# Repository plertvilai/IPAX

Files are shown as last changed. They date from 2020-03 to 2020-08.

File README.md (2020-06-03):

# In Situ Plankton Assemblage eXplorer
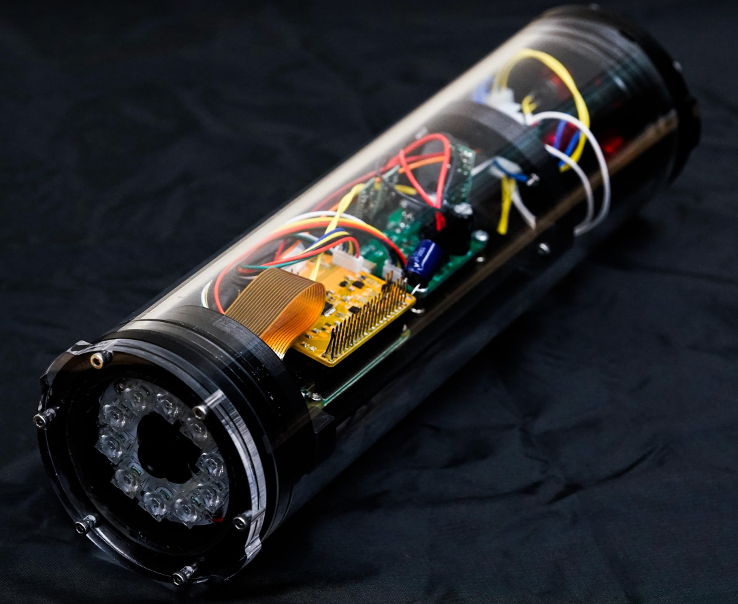
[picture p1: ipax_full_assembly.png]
Image of IPAX


This Github repository contains all information necessary to build the In Situ Plankton Assemblage eXplorer (IPAX). Here is a brief introduction to how to utilize the repository. 

# Detailed Guide

A detail building guide is given in the Building Guide subfolder. Note that this guide is written in HTML format. To read it, simply download the entire folder and use a browser to open the file [index.html](https://github.com/plertvilai/IPAX/blob/master/Building%20Guide/index.html "index.html"). 

# Fabrication Files

There are two folders containing files that are necessary for IPAX fabrication.
1. **Mechanicals** contains STL files that can be directly sent to a 3D printer to printout the mechanical parts. A STEP file is also included for users that are interested to develop the system further. The STEP file [Assembly Rev02 Revised for BES v3.step](https://github.com/plertvilai/IPAX/blob/master/Mechanicals/Assembly%20Rev02%20Revised%20for%20BES%20v3.step "Assembly Rev02 Revised for BES v3.step") contains CAD files of all the parts, including waterproof housing from Bluerobotics that can be opened with a CAD software for further development.
2. **PCBs** contains all files for the printed circuit boards in the IPAX. Each subfolder is for each PCB, and the folder fabrication contains Gerber files that can be sent directly to PCB manufacturers. Each subfolder also contains KiCAD files that users can use to develop the PCBs for fit their needs. 

# Firmware
The folder Firmware contains all software for the IPAX. 
### Control Board
This subfolder contains Arduino (.ino) files that can be uploaded to the control board of the IPAX. 
1. full_control_alwaysON is the main routine for the control board that set the Raspberry Pi to always ON.
2. full_control_interval is the main routine for the control board that turns the Raspberry Pi ON only at the specified time.
3. rtc_set is a temporary code that can be uploaded to the control board to set the real-time clock.

### Raspberry Pi
This subfolder contains Python files for the Raspberry Pi on the IPAX. 
1. connectArduino.py is a routine that allows the Raspberry Pi to communicate with the Arduino on the control board.
2. ipaxClass.py is the library for the IPAX.
3. ipaxDeploy.py is the main routine for deploying the IPAX.
4. shutdowncheck.py is the control script that allows the Raspberry Pi to be properly shutdown with an external switch on the housing and the control board.

The configuration subfolder contains all the configuration files needed to configure that Raspberry Pi.

# Bill of Materials
The folder BOM contains a single MS Excel file (.xlsx) that contains the detailed bill of materials of the IPAX.

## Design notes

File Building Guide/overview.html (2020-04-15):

# IPAX Documentation

1. Home
2. Overview

# Overview

Last updated: April, 2020

## Production Steps

This section outlines the production process of the IPAX. Though not necessarily needed to be done in this particular order, we recommend users to build an IPAX in the step as shown in the diagram below. This page provides steps for assembly process, but the detail of each step can be found in the respective page.

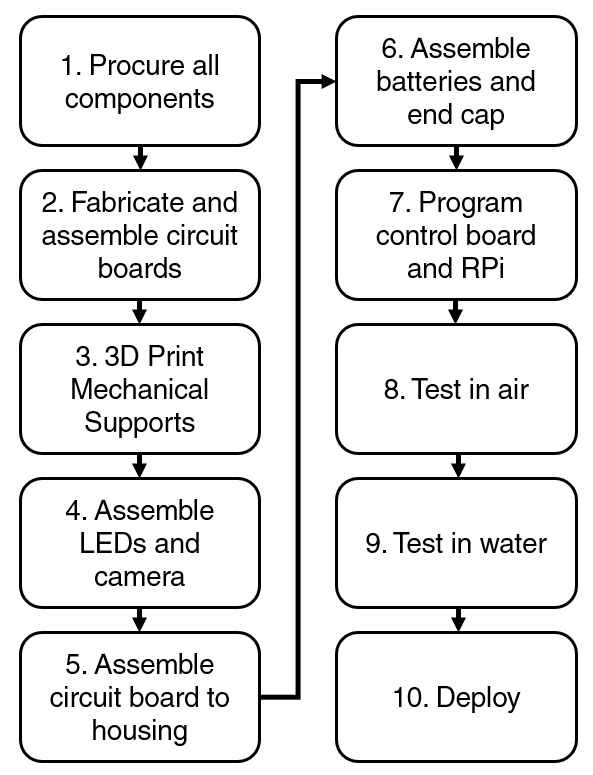
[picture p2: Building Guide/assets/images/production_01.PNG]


## 1. Procurement

The entire bill of materials for the IPAX is provided in the BOM folder. The BOM also indicates recommended vendors, though users can procure their components through any vendors.

## 2. Printed Circuit Boards

There are 3 printed circuit boards in the IPAX that need to be fabricated. The KiCAD files for all three boards are available in the PCBs folder. In each folder for each PCB, there is a folder called "Gerber" that contains gerber files that are ready to be sent to a PCB house for fabrication.

The control board and the power regulator boards can be fabricated with regular FR-4 substrate, but we strongly recommend that the LED array board should be fabricated with aluminum substrate to help with heat sink.

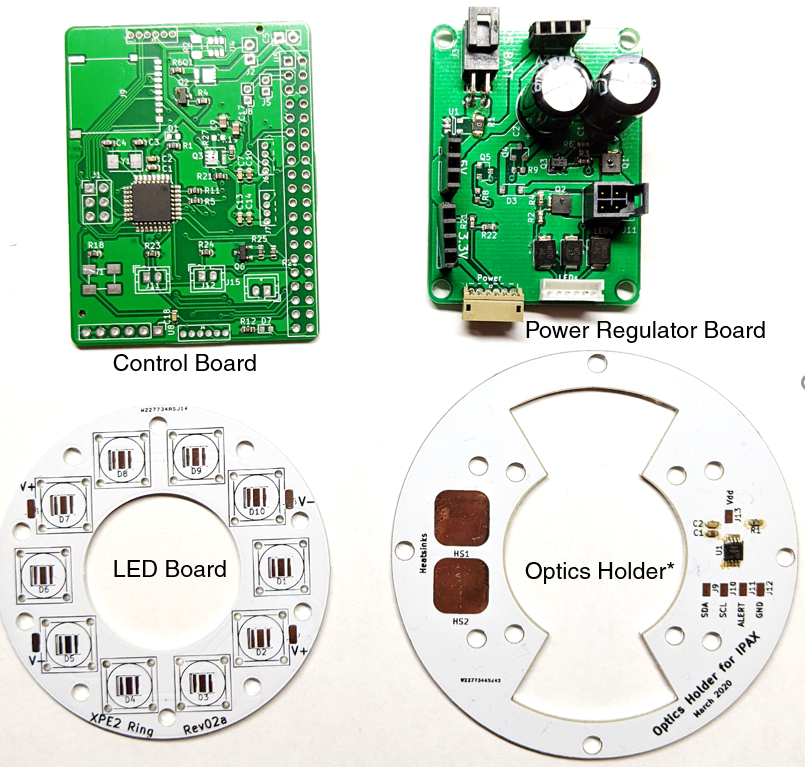
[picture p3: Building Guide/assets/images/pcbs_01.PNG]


*There is an optional 4th board called "optics holder" that is not required, but we recommend if users plan to use the IPAX for an application that requires the LED to be on for an extended period of time. This board mainly helps attach the LED array board to the aluminum flange of the housing. It will help dissipate heat from the LEDs out very quickly. However, if heating is not a problem, it can be replaced with a simple 3D printed part.

**Another optinal PCB is an SD card add-on, which will be deprecated and added directly to the control board in future revisions. However, for now, it provides the control board with an access to an SD card without the need to turn the Pi on. The SD card can be used to store environmental data and also to store configuration files.

## 3. 3D Printed Parts

There are 3 components that need to be printed out using an FDM 3D printer. The STEP files of all three components are provided in Mechanical folder, along with the STEP file for the entire assembly. Note that we use Fusion 360 as the CAD software, so there might be some issues if the files are opened with other software.

There are no special requirements for all these 3D printed parts. We use PLA material to print all of them. Note that the two battery holders shown in the picture below are identical.

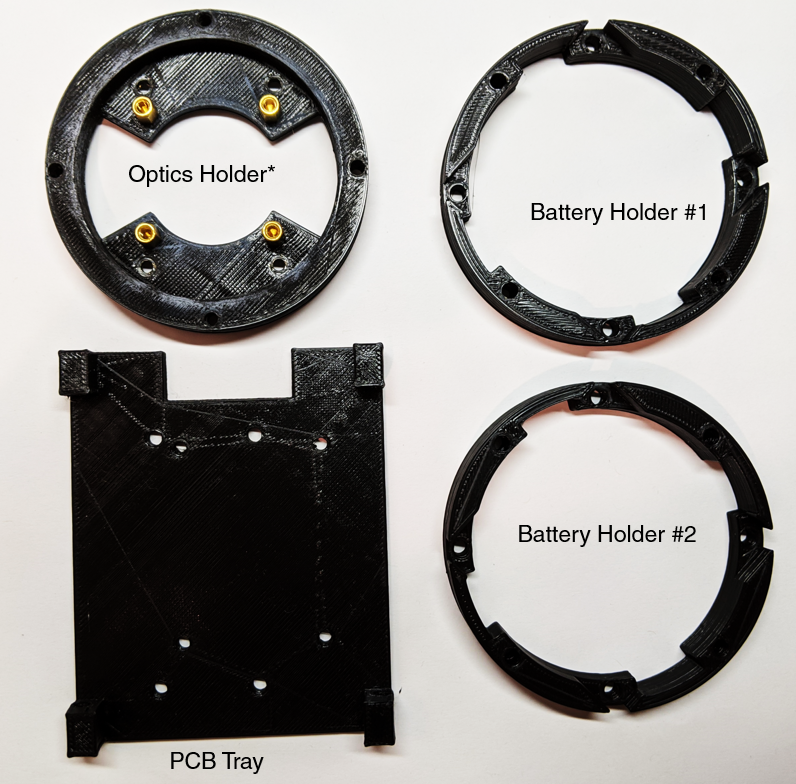
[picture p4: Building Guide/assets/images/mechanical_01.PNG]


*Optics holder can be replaced with an aluminum PCB for better heat dissipation.

## 4. LED and Camera Assembly

The LED board and the Arducam camera board can be attached to the optics holder PCB (or 3D printed part) using a set of M3 screws and standoffs as shown in the image below. The assembly can then be attached to the aluminum flange using a set screw and a screw.

Note that depending on the M12 lens, the position of the camera might need to be adjusted. The provided files are suitable for M12 lens with focal length no longer than 16mm; otherwise, the lens would be too long to fit inside the housing. The lens should be almost flat on top of the acrylic viewport to prevent the LED light from reflecting back into the camera lens.

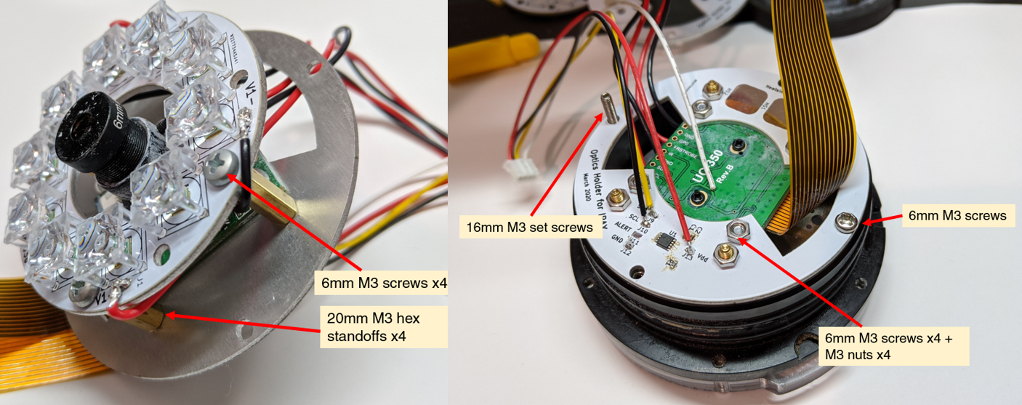
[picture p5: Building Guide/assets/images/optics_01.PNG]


## 5. PCB Tray Assembly

The Pi Zero W can be attached to the 3D printed PCB tray with a set of M2.5 standoffs (M3 does not fit through the holes on the Pi zero board). Note that this is the only place where M2.5 screws are used; the rest of the system uses M3 only.

The control board is attached directly on top of the Pi with the 40-pin GPIO headers. The power regulator board is attached to the other side of the PCB tray. Then, the entire tray is attached to the flange. Note that the bottom of the tray (the power regulator side) can be reinforced with 87mm M3 standoff (combination of multiple standoffs).

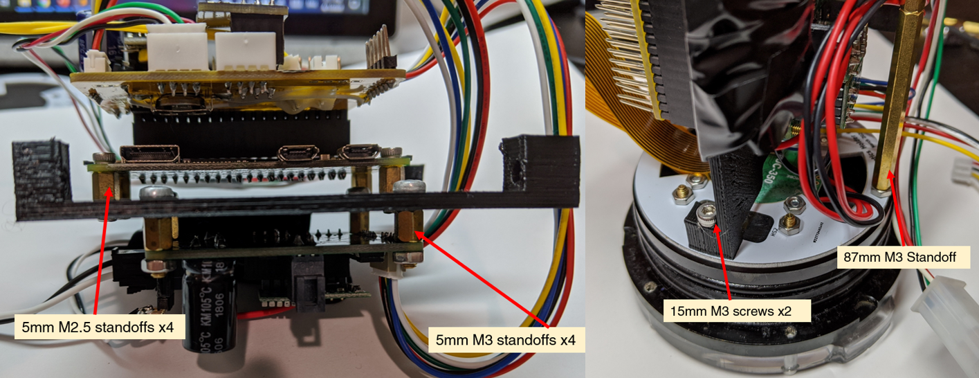
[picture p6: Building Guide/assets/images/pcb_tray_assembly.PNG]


## 6. Battery and End Cap Assembly

The battery used in this tutorial is Tenergy 31019. Other batteries will work as well, but users need to modify the 3D file for the battery holder.

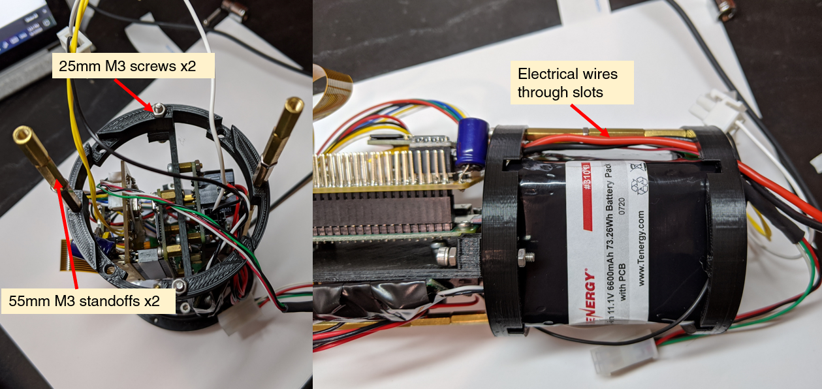
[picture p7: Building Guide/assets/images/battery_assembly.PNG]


The endcap requires at least two switches: one for main power and the other for shutdown signal. The environmental sensors are optional and can be replaced with blank screws. All wire-to-wire connections are done with Molex Minifit connectors.

Note that we do not recommend Blueorobotics vent plug, and its function can be done through a switch instead. See mechanical section for more information.

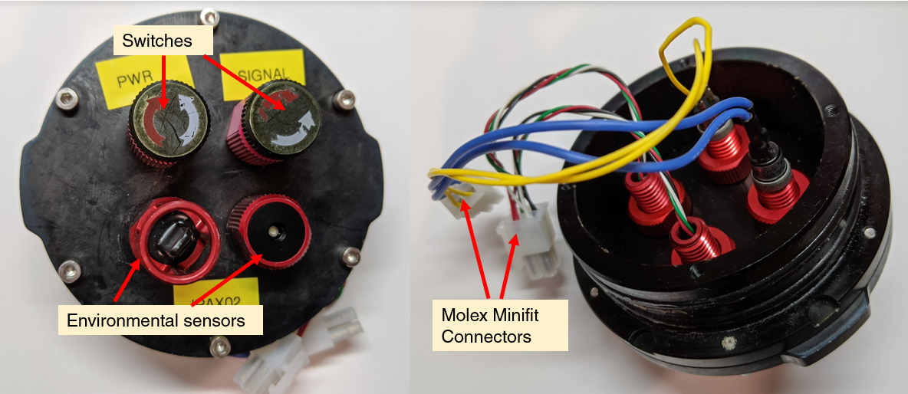
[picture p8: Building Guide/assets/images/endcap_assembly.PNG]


Here is the fully assembled internal parts of the IPAX.

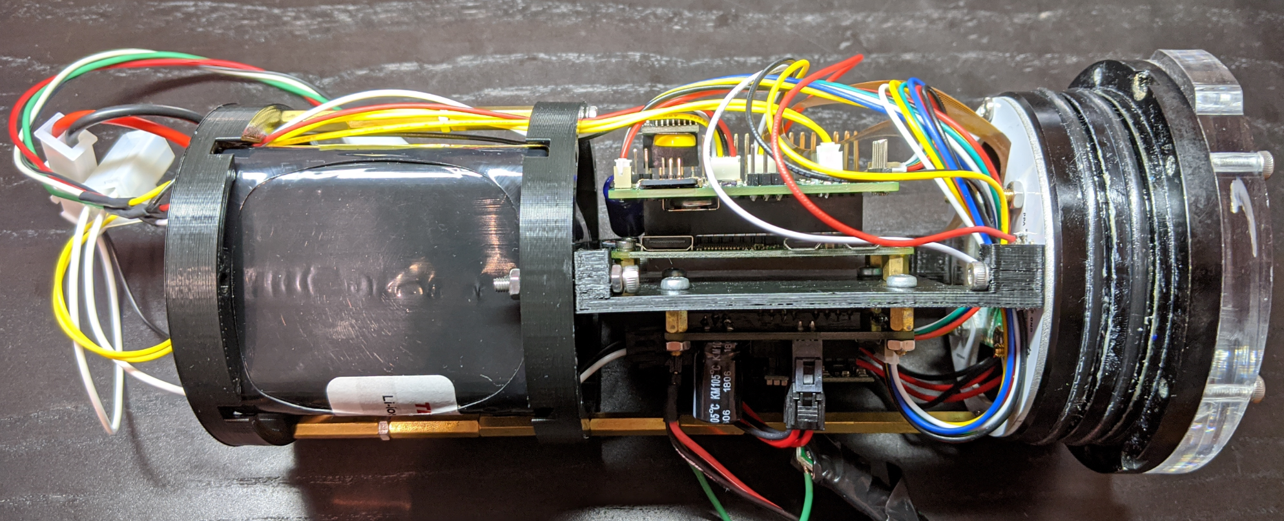
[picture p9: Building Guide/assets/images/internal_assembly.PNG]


## 7. Programming

Programming on the control board is done with Arduino platform and on the Pi Zero W is done with Python. The detail can be found on programming section.

Designed with by Xiaoying Riley (https://themes.3rdwavemedia.com/) for developers

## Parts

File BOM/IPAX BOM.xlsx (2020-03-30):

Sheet: Overview
Subsystem | Price
Control Board | 25.16135
Power Regulator Board | 31.9719
Optics and Camera | 107.404
Housing | 154
Batteries | 23.06
Miscellany | 85.48
Total | 427.07725

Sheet: Miscellany
Item | Function | Manufacturer | Part Number | Unit Price | Qunatity | Subtotal | Suggested Vendor
Raspberry Pi Zero W | Main computer | Raspberry Pi Foundation |  | 10 | 1 | 10 | https://www.adafruit.com/product/3400
Control Board PCB | 2-sided FR-4 Substrate |  |  | 2 | 1 | 2
Power Regulator Board PCB | 2-sided FR-4 Substrate |  |  | 2 | 1 | 2
LED Board | 1-sided Aluminum substrate |  |  | 5 | 1 | 5
M2.5 Screw and Hex Set | Circuit board mounts | Generic |  | 10.99 | 1 | 10.99 | https://www.amazon.com/gp/product/B075K3QBMX/ref=ppx_yo_dt_b_search_asin_title?ie=UTF8&psc=1
M3 Hex Standoff 15mm | Optics mount | Generic |  | 7.62 | 1 | 7.62 | https://www.amazon.com/gp/product/B00AO430VI/ref=ppx_yo_dt_b_search_asin_title?ie=UTF8&psc=1
M3 Hex Standoff 15mm | Optics mount | Generic |  | 6.09 | 1 | 6.09 | https://www.amazon.com/gp/product/B07H3R291C/ref=ppx_yo_dt_b_search_asin_title?ie=UTF8&psc=1
3D Printer Filament | Mechanical parts | Generic |  | 23 | 1 | 23 | https://www.amazon.com/gp/product/B00J0ECR5I/ref=ppx_yo_dt_b_asin_title_o03_s00?ie=UTF8&psc=1
M3 Screw Set | Optics mount | Generic |  | 10.79 | 1 | 10.79 | https://www.amazon.com/gp/product/B0714FLXND/ref=ppx_yo_dt_b_search_asin_title?ie=UTF8&psc=1
32GB SD card | Data storage | SanDisk |  | 7.99 | 1 | 7.99 | https://www.amazon.com/SanDisk-Ultra-microSDXC-Memory-Adapter/dp/B073JWXGNT
 |  |  |  |  |  | 85.48

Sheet: Batteries
Item | Function | Manufacturer | Part Number | Unit Price | Qunatity | Subtotal | Suggested Vendor
18650 Batteries | 3.7V 3500mAh | Samsung | SAMSUNG-35E | 4.99 | 4 | 19.96 | https://www.imrbatteries.com/samsung-35e-18650-3500mah-8a-battery/
Battery Protection Circuit | Protection circuit for 2S Lithium | Anmbest | 7071299062492 | 2 | 1 | 2 | https://www.amazon.com/gp/product/B07KSQY67X/ref=ppx_yo_dt_b_search_asin_title?ie=UTF8&psc=1
Battery Holder | Holder for 2S Lithium 18650 | TrendBox | B072HBW2XQ | 0.55 | 2 | 1.1 | https://www.amazon.com/gp/product/B0718ST7PW/ref=ppx_yo_dt_b_search_asin_title?ie=UTF8&psc=1
 |  |  |  |  |  | 23.06

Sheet: Control Board
Ref | Value | Function | Note | Manufacturer | Part Number | Unit Price | Suggested Vendors
C1 | 1uF |  | 0603 Footprint | Samsung Electro-Mechanics | CL10A105KP8NNNC | 0.04 | https://www.digikey.com/product-detail/en/samsung-electro-mechanics/CL10A105KP8NNNC/1276-1182-1-ND/3889268
C2 | 0.1uF |  | 0603 Footprint | Samsung Electro-Mechanics | C0603C104Z3VACTU | 0.032 | https://www.digikey.com/product-detail/en/kemet/C0603C104Z3VACTU/399-1100-1-ND/411375
C3 | 22pF |  | 0603 Footprint | Yageo | CC0603JRNPO8BN220 | 0.065 | https://www.digikey.com/product-detail/en/%E5%9E%88-%C3%A1/CC0603JRNPO8BN220/311-3952-1-ND/8025041
C4 | 22pF |  | 0603 Footprint | Yageo | CC0603JRNPO8BN220 | 0.065 | https://www.digikey.com/product-detail/en/%E5%9E%88-%C3%A1/CC0603JRNPO8BN220/311-3952-1-ND/8025041
C5 | 10uF |  | 0805 Footprint | KEMET | C0805C106K8PACTU | 0.117 | https://www.digikey.com/product-detail/en/kemet/C0805C106K8PACTU/399-4925-1-ND/1090920
C7 | 10nF |  | 0603 Footprint | KEMET | C0603C103M5RACTU | 0.035 | https://www.digikey.com/product-detail/en/kemet/C0603C103M5RACTU/399-7842-1-ND/3471565
C8 | 1000uF |  | Through hole | Panasonic Electronic Components | ECA-1EHG102B | 0.597 | https://www.digikey.com/product-detail/en/panasonic-electronic-components/ECA-1EHG102B/P19517CT-ND/6109415
C9 | 22uF |  | 0805 Footprint | Murata Electronics | GRM21BR61A226ME51L | 0.211 | https://www.digikey.com/product-detail/en/murata-electronics/GRM21BR61A226ME51L/490-10511-1-ND/5026441
C10 | 1uF |  | 0603 Footprint | Samsung Electro-Mechanics | CL10A105KP8NNNC | 0.04 | https://www.digikey.com/product-detail/en/samsung-electro-mechanics/CL10A105KP8NNNC/1276-1182-1-ND/3889268
C11 | 10nF |  | 0603 Footprint | KEMET | C0603C103M5RACTU | 0.035 | https://www.digikey.com/product-detail/en/kemet/C0603C103M5RACTU/399-7842-1-ND/3471565
C12 | 1uF |  | 0603 Footprint | Samsung Electro-Mechanics | CL10A105KP8NNNC | 0.04 | https://www.digikey.com/product-detail/en/samsung-electro-mechanics/CL10A105KP8NNNC/1276-1182-1-ND/3889268
C13 | 10nF |  | 0603 Footprint | KEMET | C0603C103M5RACTU | 0.035 | https://www.digikey.com/product-detail/en/kemet/C0603C103M5RACTU/399-7842-1-ND/3471565
C14 | 1uF |  | 0603 Footprint | Samsung Electro-Mechanics | CL10A105KP8NNNC | 0.04 | https://www.digikey.com/product-detail/en/samsung-electro-mechanics/CL10A105KP8NNNC/1276-1182-1-ND/3889268
C15 | 10nF |  | 0603 Footprint | KEMET | C0603C103M5RACTU | 0.035 | https://www.digikey.com/product-detail/en/kemet/C0603C103M5RACTU/399-7842-1-ND/3471565
C16 | 1uF |  | 0603 Footprint | Samsung Electro-Mechanics | CL10A105KP8NNNC | 0.04 | https://www.digikey.com/product-detail/en/samsung-electro-mechanics/CL10A105KP8NNNC/1276-1182-1-ND/3889268
C17 | 22uF |  | 0805 Footprint | Murata Electronics | GRM21BR61A226ME51L | 0.211 | https://www.digikey.com/product-detail/en/murata-electronics/GRM21BR61A226ME51L/490-10511-1-ND/5026441
C18 | 0.1uF |  | 0603 Footprint | Samsung Electro-Mechanics | C0603C104Z3VACTU | 0.032 | https://www.digikey.com/product-detail/en/kemet/C0603C104Z3VACTU/399-1100-1-ND/411375
D1 | Yellow LED | Arduino LED indicator | 0603 Footprint | Würth Elektronik | 150060YS75000 | 0.14 | https://www.digikey.com/product-detail/en/w%C3%BCrth-elektronik/150060YS75000/732-4981-1-ND/4489907
D3 | Red LED | Power fault indicator | 0603 Footprint | Würth Elektronik | 150060RS75000 | 0.14 | https://www.digikey.com/product-detail/en/w%C3%BCrth-elektronik/150060RS75000/732-4978-1-ND/4489899
D7 | Blue LED | Pi LED indicator | 0603 Footprint | Würth Elektronik | 150060BS75000 | 0.16 | https://www.digikey.com/product-detail/en/w%C3%BCrth-elektronik/150060BS75000/732-4966-1-ND/4489893
J1 | Conn_02x03_Odd_Even | ISP Connector | 2.54mm 2 rows pitch male header generic | Harwin Inc. | M20-9980346 | 0.229 | https://www.digikey.com/product-detail/en/harwin-inc/M20-9980346/952-2121-ND/3728085
J2 | Conn_01x02_Male | Raspberry Pi Power Jumper | 2.54mm pitch male header generic |  |  | 0.0375 | https://www.digikey.com/product-detail/en/sullins-connector-solutions/PRPC040SFAN-RC/S1211EC-40-ND/2775334
J3 | Conn_01x06_Male | Inter-board connector |  | JST Sales America | B6B-ZR(LF)(SN) | 0.262 | https://www.digikey.com/product-detail/en/jst-sales-america-inc/B6B-ZR-LF-SN/455-1661-ND/926568
J4 | Conn_01x06_Male | Inter-board connector |  | JST Sales America | B6B-ZR(LF)(SN) | 0.262 | https://www.digikey.com/product-detail/en/jst-sales-america-inc/B6B-ZR-LF-SN/455-1661-ND/926568
J6 | Conn_01x04_Male | I2C Header |  | JST Sales America |  | 0.227 | https://www.digikey.com/product-detail/en/jst-sales-america-inc/B4B-PH-K-S-LF-SN/455-1706-ND/926613
J7 | Conn_01x04_Male | I2C Header |  | JST Sales America |  | 0.227 | https://www.digikey.com/product-detail/en/jst-sales-america-inc/B4B-PH-K-S-LF-SN/455-1706-ND/926613
J11 | Conn_01x02_Male | Push button connector |  | JST Sales America |  | 0.162 | https://www.digikey.com/product-detail/en/jst-sales-america-inc/B2B-PH-K-S-LF-SN/455-1704-ND/926611
J12 | Conn_01x02_Male | Push button connector |  | JST Sales America |  | 0.162 | https://www.digikey.com/product-detail/en/jst-sales-america-inc/B2B-PH-K-S-LF-SN/455-1704-ND/926611
J14 | Conn_01x03_Male | Hall effect connector |  | JST Sales America | B3B-PH-K-S(LF)(SN) | 0.19 | https://www.digikey.com/product-detail/en/jst-sales-america-inc/B3B-PH-K-S-LF-SN/455-1705-ND/926612
J15 | Conn_01x02_Male | Fan Connector |  | JST Sales America |  | 0.162 | https://www.digikey.com/product-detail/en/jst-sales-america-inc/B2B-PH-K-S-LF-SN/455-1704-ND/926611
Q1 | PMOS | Power FET |  | Diodes Incorporated | DMP2008UFG-7 | 0.473 | https://www.digikey.com/product-detail/en/diodes-incorporated/DMP2008UFG-7/DMP2008UFG-7DICT-ND/3720111
Q2 | Q_NMOS_GSD | Power FET |  | Diodes Incorporated | DMN1019USN-7 | 0.347 | https://www.digikey.com/product-detail/en/diodes-incorporated/DMN1019USN-7/DMN1019USN-7DICT-ND/4898886
Q3 | PMOS | Power FET |  | Diodes Incorporated | DMP2008UFG-7 | 0.473 | https://www.digikey.com/product-detail/en/diodes-incorporated/DMP2008UFG-7/DMP2008UFG-7DICT-ND/3720111
Q6 | Q_NMOS_GSD | Power FET |  | Diodes Incorporated | DMN1019USN-7 | 0.347 | https://www.digikey.com/product-detail/en/diodes-incorporated/DMN1019USN-7/DMN1019USN-7DICT-ND/4898886
R1 | 499R |  | 0603 Footprint | Stackpole Electronics Inc | RNCP0603FTD499R | 0.0273 | https://www.digikey.com/product-detail/en/stackpole-electronics-inc/RNCP0603FTD499R/RNCP0603FTD499RCT-ND/2240437
R2 | 0.01R | Current sense resistor | 1206 Footprint | Panasonic Electronic Components | ERJ-8BWFR010V | 0.547 | https://www.digikey.com/product-detail/en/panasonic-electronic-components/ERJ-8BWFR010V/P-010AUCT-ND/1711682
R3 | 0.01R | Current sense resistor | 1206 Footprint | Panasonic Electronic Components | ERJ-8BWFR010V | 0.547 | https://www.digikey.com/product-detail/en/panasonic-electronic-components/ERJ-8BWFR010V/P-010AUCT-ND/1711682
R4 | 499R |  | 0603 Footprint | Stackpole Electronics Inc | RNCP0603FTD499R | 0.0273 | https://www.digikey.com/product-detail/en/stackpole-electronics-inc/RNCP0603FTD499R/RNCP0603FTD499RCT-ND/2240437
R5 | 499R |  | 0603 Footprint | Stackpole Electronics Inc | RNCP0603FTD499R | 0.0273 | https://www.digikey.com/product-detail/en/stackpole-electronics-inc/RNCP0603FTD499R/RNCP0603FTD499RCT-ND/2240437
R6 | 10k |  | 0603 Footprint | Yageo | RC0603JR-0710KL | 0.019 | https://www.digikey.com/product-detail/en/%E5%9E%88-%C3%A1/RC0603JR-0710KL/311-10KGRCT-ND/729647
R7 | 10k |  | 0603 Footprint | Yageo | RC0603JR-0710KL | 0.019 | https://www.digikey.com/product-detail/en/%E5%9E%88-%C3%A1/RC0603JR-0710KL/311-10KGRCT-ND/729647
R8 | 10k |  | 0603 Footprint | Yageo | RC0603JR-0710KL | 0.019 | https://www.digikey.com/product-detail/en/%E5%9E%88-%C3%A1/RC0603JR-0710KL/311-10KGRCT-ND/729647
R9 | 10k |  | 0603 Footprint | Yageo | RC0603JR-0710KL | 0.019 | https://www.digikey.com/product-detail/en/%E5%9E%88-%C3%A1/RC0603JR-0710KL/311-10KGRCT-ND/729647
R10 | 10k |  | 0603 Footprint | Yageo | RC0603JR-0710KL | 0.019 | https://www.digikey.com/product-detail/en/%E5%9E%88-%C3%A1/RC0603JR-0710KL/311-10KGRCT-ND/729647
R11 | 499R |  | 0603 Footprint | Stackpole Electronics Inc | RNCP0603FTD499R | 0.0273 | https://www.digikey.com/product-detail/en/stackpole-electronics-inc/RNCP0603FTD499R/RNCP0603FTD499RCT-ND/2240437
R12 | 499R |  | 0603 Footprint | Stackpole Electronics Inc | RNCP0603FTD499R | 0.0273 | https://www.digikey.com/product-detail/en/stackpole-electronics-inc/RNCP0603FTD499R/RNCP0603FTD499RCT-ND/2240437
R13 | 10k |  | 0603 Footprint | Yageo | RC0603JR-0710KL | 0.019 | https://www.digikey.com/product-detail/en/%E5%9E%88-%C3%A1/RC0603JR-0710KL/311-10KGRCT-ND/729647
R18 | 10k |  | 0603 Footprint | Yageo | RC0603JR-0710KL | 0.019 | https://www.digikey.com/product-detail/en/%E5%9E%88-%C3%A1/RC0603JR-0710KL/311-10KGRCT-ND/729647
R19 | 10k |  | 0603 Footprint | Yageo | RC0603JR-0710KL | 0.019 | https://www.digikey.com/product-detail/en/%E5%9E%88-%C3%A1/RC0603JR-0710KL/311-10KGRCT-ND/729647
R20 | 10k |  | 0603 Footprint | Yageo | RC0603JR-0710KL | 0.019 | https://www.digikey.com/product-detail/en/%E5%9E%88-%C3%A1/RC0603JR-0710KL/311-10KGRCT-ND/729647
R21 | 499R |  | 0603 Footprint | Stackpole Electronics Inc | RNCP0603FTD499R | 0.0273 | https://www.digikey.com/product-detail/en/stackpole-electronics-inc/RNCP0603FTD499R/RNCP0603FTD499RCT-ND/2240437
R22 | 499R |  | 0603 Footprint | Stackpole Electronics Inc | RNCP0603FTD499R | 0.0273 | https://www.digikey.com/product-detail/en/stackpole-electronics-inc/RNCP0603FTD499R/RNCP0603FTD499RCT-ND/2240437
R23 | 10k |  | 0603 Footprint | Yageo | RC0603JR-0710KL | 0.019 | https://www.digikey.com/product-detail/en/%E5%9E%88-%C3%A1/RC0603JR-0710KL/311-10KGRCT-ND/729647
R24 | 10k |  | 0603 Footprint | Yageo | RC0603JR-0710KL | 0.019 | https://www.digikey.com/product-detail/en/%E5%9E%88-%C3%A1/RC0603JR-0710KL/311-10KGRCT-ND/729647
R25 | 10k |  | 0603 Footprint | Yageo | RC0603JR-0710KL | 0.019 | https://www.digikey.com/product-detail/en/%E5%9E%88-%C3%A1/RC0603JR-0710KL/311-10KGRCT-ND/729647
R27 | 0R | Jumper | 0603 Footprint | Yageo | RC0603JR-0710KL | 0.019 | https://www.digikey.com/product-detail/en/%E5%9E%88-%C3%A1/RC0603JR-070RL/311-0-0GRCT-ND/729622
R28 | 10k |  | 0603 Footprint | Yageo | RC0603JR-0710KL | 0.019 | https://www.digikey.com/product-detail/en/%E5%9E%88-%C3%A1/RC0603JR-0710KL/311-10KGRCT-ND/729647
R29 | 10k |  | 0603 Footprint | Yageo | RC0603JR-0710KL | 0.019 | https://www.digikey.com/product-detail/en/%E5%9E%88-%C3%A1/RC0603JR-0710KL/311-10KGRCT-ND/729647
R30 | 10k |  | 0603 Footprint | Yageo | RC0603JR-0710KL | 0.019 | https://www.digikey.com/product-detail/en/%E5%9E%88-%C3%A1/RC0603JR-0710KL/311-10KGRCT-ND/729647
SW1 | SW_DPST | For testing only |  |  |  | 0.06 | https://www.amazon.com/Uxcell-a12011500ux0296-Momentary-Tactile-Surface/dp/B008DS1FQO
U1 | ATmega328P-AU | Main microcontroller |  |  |  | 1.84 | https://www.digikey.com/product-detail/en/microchip-technology/ATMEGA328P-AU/ATMEGA328P-AU-ND/1832260
U3 | NCP361 | Power surge protector |  |  |  | 0.594 | https://www.digikey.com/product-detail/en/on-semiconductor/NCP361SNT1G/NCP361SNT1GOSCT-ND/1894072
U4 | INA181 | Current sense circuit |  |  |  | 0.627 | https://www.digikey.com/product-detail/en/texas-instruments/INA181A1IDBVR/296-47656-1-ND/8133025
U5 | 2x20 Female Header | Raspberry Pi connector | 2.54mm pitch 2 row female header |  |  | 0.3 | https://www.amazon.com/Antrader-2-54mm-2x20Pin-Female-Connector/dp/B07D48WZTR
U6 | I2C Header | Extra connector for I2C device | 2.54mm pitch male header generic |  |  | 0.0675 | https://www.digikey.com/product-detail/en/sullins-connector-solutions/PRPC040SFAN-RC/S1211EC-40-ND/2775334
U7 | Coin cell holder | CR1205 |  |  |  | 0.399 | https://www.digikey.com/product-detail/en/mpd-memory-protection-devices/BK-870/BK-870-ND/3829737
U8 | FTDI_Basic | External UART | 2.54mm pitch male header generic |  |  | 0.10125 | https://www.digikey.com/product-detail/en/sullins-connector-solutions/PRPC040SFAN-RC/S1211EC-40-ND/2775334
U9 | DS3231MZ | Real time clock |  |  |  | 7.125 | https://www.digikey.com/product-detail/en/maxim-integrated/DS3231MZ/DS3231MZ-ND/2754396
U10 | BME280 | Environmental sensor |  |  |  | 5.776 | https://www.digikey.com/product-detail/en/bosch-sensortec/BME280/828-1063-1-ND/6136314
Y1 | Crystal | 8MHz crystal for MCU |  | Abracon LLC | ABM3-8.000MHZ-D2Y-T | 1.012 | https://www.digikey.com/product-detail/en/ABM3-8.000MHZ-D2Y-T/535-10630-1-ND/2344632?so=58040267
 |  |  |  |  |  | 25.16135

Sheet: Housing
Item | Function | Manufacturer | Part Number | Unit Price | Qunatity | Subtotal | Suggested Vendor
Aluminum End Cap | Sensor and switch mount | Bluerobotics |  | 12 | 1 | 12 | https://bluerobotics.com/store/watertight-enclosures/3-series/wte3-m-end-cap-4-hole-r1/
Acrylic End Cap | Viewport | Bluerobotics |  | 10 | 1 | 10 | https://bluerobotics.com/store/watertight-enclosures/3-series/wte3-p-end-cap-r1/
O-ring Flange | Waterproofing | Bluerobotics |  | 24 | 2 | 48 | https://bluerobotics.com/store/watertight-enclosures/3-series/o-ring-flange-3-series/
Cast Acrylic Tube | 3" Diameter 11.75" Length | Bluerobotics |  | 46 | 1 | 46 | https://bluerobotics.com/store/watertight-enclosures/3-series/wte3-p-tube-12-r1/
Switch | Waterproof switch | Bluerobotics |  | 15 | 2 | 30 | https://bluerobotics.com/store/comm-control-power/switch/switch-10-5a-r1/
Penetrator Blank | Placeholder for extra sensors and switches | Bluerobotics |  | 4 | 2 | 8 | https://bluerobotics.com/store/cables-connectors/penetrators/penetrator-blank-10-25-a-r2/
 |  |  |  |  |  | 154
Temperature Sensor |  | Bluerobotics | CELSIUS-SENSOR-R1-RP | 60 | 1 | 60 | https://bluerobotics.com/store/sensors-sonars-cameras/sensors/celsius-sensor-r1/
Depth Sensor | Has temperature sensor | Bluerobotics | BAR30-SENSOR-R1-RP | 72 | 1 | 72 | https://bluerobotics.com/store/sensors-sonars-cameras/sensors/bar30-sensor-r1/

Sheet: Power Regulator
Ref | Value | Function | Note | Manufacturer | Part Number | Unit Price | Suggested Vendors
C1 | 1000uF |  | Through hole | Panasonic Electronic Components | ECA-1EHG102B | 0.597 | https://www.digikey.com/product-detail/en/panasonic-electronic-components/ECA-1EHG102B/P19517CT-ND/6109415
C2 | 1000uF |  | Through hole | Panasonic Electronic Components | ECA-1EHG102B | 0.597 | https://www.digikey.com/product-detail/en/panasonic-electronic-components/ECA-1EHG102B/P19517CT-ND/6109415
D1 | SMBJ5.0CA | Transient Voltage Suppresor for RPi GPIO Protection |  | Diodes Incorporated | SMBJ5.0CA-13-F | 0.285 | https://www.digikey.com/product-detail/en/diodes-incorporated/SMBJ5-0CA-13-F/SMBJ5-0CA-FDICT-ND/750045
D2 | SMBJ5.0CA | Transient Voltage Suppresor for RPi GPIO Protection |  | Diodes Incorporated | SMBJ5.0CA-13-F | 0.285 | https://www.digikey.com/product-detail/en/diodes-incorporated/SMBJ5-0CA-13-F/SMBJ5-0CA-FDICT-ND/750045
D3 | NSI450-20AT1G | Current control diode |  | ON Semiconductor | NSI45020AT1G | 0.414 | https://www.digikey.com/product-detail/en/on-semiconductor/NSI45020AT1G/NSI45020AT1GOSCT-ND/2096225
D4 | SMBJ5.0CA | Transient Voltage Suppresor for RPi GPIO Protection |  | Diodes Incorporated | SMBJ5.0CA-13-F | 0.285 | https://www.digikey.com/product-detail/en/diodes-incorporated/SMBJ5-0CA-13-F/SMBJ5-0CA-FDICT-ND/750045
J1 | Conn_01x03_Female | 5V Regulator Board from Pololu |  | Pololu Robotics & Electronics | 2119 | 4.95 | https://www.pololu.com/product/2119
J2 | Conn_01x06_Female | Inter-board connector |  | JST Sales America | B6B-ZR(LF)(SN) | 0.262 | https://www.digikey.com/product-detail/en/jst-sales-america-inc/B6B-ZR-LF-SN/455-1661-ND/926568
J3 | Conn_01x04_Male | Batter Power Connector |  | Molex | 1053141204 | 1.258 | https://www.digikey.com/product-detail/en/molex/1053141204/WM14976-ND/6131618
J4 | Conn_01x01_Male | Hole for fastening screw |  |  |  | 0
J5 | Conn_01x01_Male | Hole for fastening screw |  |  |  | 0
J6 | Conn_01x01_Male | Hole for fastening screw |  |  |  | 0
J7 | Conn_01x01_Male | Hole for fastening screw |  |  |  | 0
J8 | Conn_01x03_Female | Adjustable Boost Regulator Board from Pololu |  | Pololu Robotics & Electronics | 799 | 11.95 | https://www.pololu.com/product/799
J9 | Conn_01x04_Female | 3.3V Regulator Board from Pololu |  | Pololu Robotics & Electronics | 2122 | 5.95 | https://www.pololu.com/product/2122
J10 | Conn_01x06_Male | Inter-board connector |  | JST Sales America | B6B-ZR(LF)(SN) | 0.262 | https://www.digikey.com/product-detail/en/jst-sales-america-inc/B6B-ZR-LF-SN/455-1661-ND/926568
J11 | Conn_01x04_Male | LED connector |  | Molex | 1053101204 | 1.228 | https://www.digikey.com/product-detail/en/molex/1053101204/WM14969-ND/6131611
Q1 | PMOS | Power FET |  | Diodes Incorporated | DMP2008UFG-7 | 0.473 | https://www.digikey.com/product-detail/en/diodes-incorporated/DMP2008UFG-7/DMP2008UFG-7DICT-ND/3720111
Q2 | NMOS | Power FET |  | Diodes Incorporated | DMG7430LFG-7 | 0.309 | https://www.digikey.com/product-detail/en/diodes-incorporated/DMG7430LFG-7/DMG7430LFG-7DICT-ND/2952003
Q3 | Q_NMOS_GSD | Power FET |  | Diodes Incorporated | DMN1019USN-7 | 0.347 | https://www.digikey.com/product-detail/en/diodes-incorporated/DMN1019USN-7/DMN1019USN-7DICT-ND/4898886
Q4 | Q_PMOS_GSD | Power FET |  | Diodes Incorporated | DMP3130L-7 | 0.332 | https://www.digikey.com/product-detail/en/diodes-incorporated/DMP3130L-7/DMP3130LDICT-ND/2052811
Q5 | Q_NMOS_GSD | Power FET |  | Diodes Incorporated | DMN1019USN-7 | 0.347 | https://www.digikey.com/product-detail/en/diodes-incorporated/DMN1019USN-7/DMN1019USN-7DICT-ND/4898886
R1 | 0.01R | Current sense resistor | 1206 Footprint | Panasonic Electronic Components | ERJ-8BWFR010V | 0.547 | https://www.digikey.com/product-detail/en/panasonic-electronic-components/ERJ-8BWFR010V/P-010AUCT-ND/1711682
R2 | 499R |  | 0603 Footprint | Stackpole Electronics Inc | RNCP0603FTD499R | 0.0273 | https://www.digikey.com/product-detail/en/stackpole-electronics-inc/RNCP0603FTD499R/RNCP0603FTD499RCT-ND/2240437
R3 | 499R |  | 0603 Footprint | Stackpole Electronics Inc | RNCP0603FTD499R | 0.0273 | https://www.digikey.com/product-detail/en/stackpole-electronics-inc/RNCP0603FTD499R/RNCP0603FTD499RCT-ND/2240437
R4 | 10k |  | 0603 Footprint | Yageo | RC0603JR-0710KL | 0.019 | https://www.digikey.com/product-detail/en/%E5%9E%88-%C3%A1/RC0603JR-0710KL/311-10KGRCT-ND/729647
R6 | 10k |  | 0603 Footprint | Yageo | RC0603JR-0710KL | 0.019 | https://www.digikey.com/product-detail/en/%E5%9E%88-%C3%A1/RC0603JR-0710KL/311-10KGRCT-ND/729647
R7 | 10R |  | 0603 Footprint | Yageo | RC0603JR-0710KL | 0.019 | https://www.digikey.com/product-detail/en/%E5%9E%88-%C3%A1/RC0603JR-0710KL/311-10KGRCT-ND/729647
R8 | 499R |  | 0603 Footprint | Stackpole Electronics Inc | RNCP0603FTD499R | 0.0273 | https://www.digikey.com/product-detail/en/stackpole-electronics-inc/RNCP0603FTD499R/RNCP0603FTD499RCT-ND/2240437
R9 | 10k |  | 0603 Footprint | Yageo | RC0603JR-0710KL | 0.019 | https://www.digikey.com/product-detail/en/%E5%9E%88-%C3%A1/RC0603JR-0710KL/311-10KGRCT-ND/729647
R21 | 10k |  | 0603 Footprint | Yageo | RC0603JR-0710KL | 0.019 | https://www.digikey.com/product-detail/en/%E5%9E%88-%C3%A1/RC0603JR-0710KL/311-10KGRCT-ND/729647
R22 | 20k |  | 604 Footprint | Yageo | RC0603FR-0720KL | 0.023 | https://www.digikey.com/product-detail/en/%E5%9E%88%ED%9B%87/RC0603FR-0720KL/311-20-0KHRCT-ND/729987
U1 | MAX9938 | Current sense |  | Maxim Integrated | MAX9938HEUK+T | 1.094 | https://www.digikey.com/product-detail/en/maxim-integrated/MAX9938HEUK-T/MAX9938HEUK-TCT-ND/2234739
 |  |  |  |  |  | 31.9719

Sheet: Optics
Item | Function | Manufacturer | Part Number | Unit Price | Quantity | Subtotal | Suggested Vendors
Focusing Lens | Narrow spot | Carclo | 10412 | 1.125 | 10 | 11.25 | https://www.arrow.com/en/products/10412/carclo-technical-plastics
LEDs | 6500K White LEDs | Cree | XPEBWT-L1-0000-00EE1 | 0.9164 | 10 | 9.164 | https://www.arrow.com/en/products/xpebwt-l1-0000-00ee1/cree
Camera | IMX219 with M12 Mount | Arducam | B0103 | 69.99 | 1 | 69.99 | https://dlscorp.com/product-category/camera-components/camera-boards/csi-boards/
M12 Lens | 4.0mm F2.0 5MP | M12Lenses | PT-0420CW-5MP | 17 | 1 | 17 | http://www.m12lenses.com/4-0mm-F2-0-5MP-M12-Mount-CCTV-Lens-p/pt-0420cw-5mp.htm
 |  |  |  |  |  | 107.404

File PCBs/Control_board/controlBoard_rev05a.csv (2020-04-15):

Comment | Designator | Footprint | LCSC Part Number
1uF | C1,C12,C16,C10,C14 | Capacitor_SMD:C_0603_1608Metric | C15849
10nF | C11,C15,C7,C13 | Capacitor_SMD:C_0603_1608Metric | C57112
0.1uF | C2,C18 | Capacitor_SMD:C_0603_1608Metric | C14663
22pF | C3,C4 | Capacitor_SMD:C_0603_1608Metric | C1653
CP | C5 | Connector_PinHeader_2.54mm:PinHeader_1x02_P2.54mm_Vertical
22uF | C9,C17 | Capacitor_SMD:C_0805_2012Metric | C45783
LED | D7,D1 | LED_SMD:LED_0603_1608Metric
Conn_02x03_Odd_Even | J1 | Connector_PinHeader_2.54mm:PinHeader_2x03_P2.54mm_Vertical
Conn_01x02_Male | J15,J11,J12 | Connector_JST:JST_PH_B2B-PH-K_1x02_P2.00mm_Vertical
Conn_01x02_Male | J2 | Connector_PinHeader_2.54mm:PinHeader_1x02_P2.54mm_Vertical
Conn_01x06_Male | J3,J4 | myLib:conn_1x06_1.5mm
Conn_01x02_Female | J5,J8 | Connector_PinHeader_2.00mm:PinHeader_1x02_P2.00mm_Vertical
Conn_01x04_Male | J6,J7 | conn:conn_1x04_1.5mm
Micro_SD_Card | J9 | myLib:DM3AT_microSD
PMOS | Q1,Q3 | Package_SON:Diodes_PowerDI3333-8
Q_NMOS_GSD | Q2 | Package_TO_SOT_SMD:SOT-23 | C382335
Q_NMOS_GSD | Q6 | myLib:SOT-23-3 | C382335
400R | R12,R5,R11,R1,R4,R21,R22 | Resistor_SMD:R_0603_1608Metric | C23193
0.01R | R2 | Resistor_SMD:R_1206_3216Metric
jumper | R27 | Resistor_SMD:R_0603_1608Metric
10k | R9,R10,R3,R6,R19,R25,R18,R23,R24,R28,R29,R30 | Resistor_SMD:R_0603_1608Metric | C25804
SW_DPST | SW1 | myLib:SMD_pushbutton | C318888
ATmega328P-AU | U1 | Package_QFP:TQFP-32_7x7mm_P0.8mm | C14877
BME280 | U10 | Package_LGA:Bosch_LGA-8_2.5x2.5mm_P0.65mm_ClockwisePinNumbering
INA181 | U4 | Package_TO_SOT_SMD:SOT-23-6
Pi_Header | U5 | myLib:RPi_Cobbler
coin_cell | U7 | myLib:BK870_CR1025holder
FTDI_Basic | U8 | Connector_PinHeader_2.54mm:PinHeader_1x06_P2.54mm_Vertical
DS3231MZ | U9 | Package_SO:SOIC-8_3.9x4.9mm_P1.27mm
Crystal | Y1 | Crystal:Crystal_SMD_Abracon_ABM3-2Pin_5.0x3.2mm

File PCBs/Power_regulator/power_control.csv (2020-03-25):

Source: | C:\Users\PichayaLertvilai\Google Drive\Scripps\Jaffe Lab\PUV\PCBs\powerControl_rev03\powerControl.sch
Date: | 3/8/2020 3:08:50 PM
Tool: | Eeschema (5.0.2)-1
Component Count: | 33
Ref | Value | Footprint | Datasheet | Manufacturer | Vendor
C1 | 470uF | Capacitor_THT:CP_Radial_D10.0mm_P5.00mm | ~
C2 | 470uF | Capacitor_THT:CP_Radial_D10.0mm_P5.00mm | ~
D1 | SMBJ5.0CA | myLib:DO-214AA | ~
D2 | SMBJ5.0CA | myLib:DO-214AA | ~
D3 | NSI450-20AT1G | Diode_SMD:D_SOD-123 | ~
D4 | SMBJ5.0CA | myLib:DO-214AA | ~
J1 | Conn_01x03_Female | Connector_PinHeader_2.54mm:PinHeader_1x03_P2.54mm_Vertical | ~
J2 | Conn_01x06_Female | myLib:conn_1x06_1.5mm | ~
J3 | Conn_01x04_Male | Connector_Molex:Molex_Nano-Fit_105314-xx04_2x02_P2.50mm_Horizontal | ~
J4 | Conn_01x01_Male | myLib:SCREW_4 | ~
J5 | Conn_01x01_Male | myLib:SCREW_4 | ~
J6 | Conn_01x01_Male | myLib:SCREW_4 | ~
J7 | Conn_01x01_Male | myLib:SCREW_4 | ~
J8 | Conn_01x03_Female | Connector_PinHeader_2.54mm:PinHeader_1x03_P2.54mm_Vertical | ~
J9 | Conn_01x04_Female | Connector_PinHeader_2.54mm:PinHeader_1x04_P2.54mm_Vertical | ~
J10 | Conn_01x06_Male | myLib:conn_1x06_1.5mm | ~
J11 | Conn_01x04_Male | Connector_Molex:Molex_Nano-Fit_105310-xx04_2x02_P2.50mm_Vertical | ~
Q1 | PMOS | Package_SON:Diodes_PowerDI3333-8 | http://www.vishay.com/docs/70209/70209.pdf
Q2 | NMOS | Package_SON:Diodes_PowerDI3333-8 | https://www.fairchildsemi.com/datasheets/2N/2N7000.pdf
Q3 | Q_NMOS_GSD | Package_TO_SOT_SMD:SOT-23 | ~
Q4 | Q_PMOS_GSD | Package_TO_SOT_SMD:SOT-23 | ~
Q5 | Q_NMOS_GSD | Package_TO_SOT_SMD:SOT-23 | ~
R1 | 0.01R | Resistor_SMD:R_1206_3216Metric | ~
R2 | 400R | Resistor_SMD:R_0603_1608Metric
R3 | 400R | Resistor_SMD:R_0603_1608Metric
R4 | 10k | Resistor_SMD:R_0603_1608Metric
R6 | 10k | Resistor_SMD:R_0603_1608Metric
R7 | 10R | Resistor_SMD:R_1206_3216Metric
R8 | 400R | Resistor_SMD:R_0603_1608Metric
R9 | 10k | Resistor_SMD:R_0603_1608Metric
R21 | 10k | Resistor_SMD:R_0603_1608Metric | ~
R22 | 20k | Resistor_SMD:R_0603_1608Metric | ~
U1 | MAX9938 | myLib:SOT-23-5 | DOCUMENTATION

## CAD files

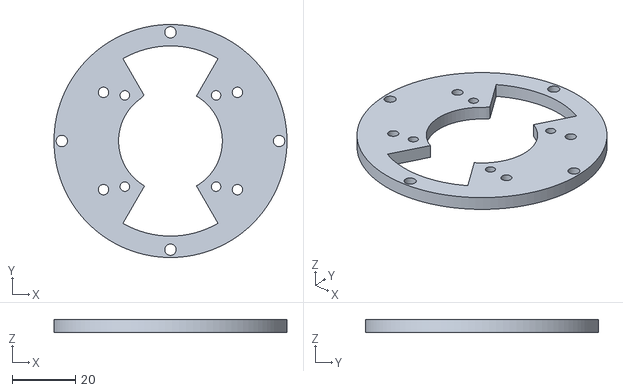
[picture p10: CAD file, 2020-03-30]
Mechanicals/Optics Holder.stl
73.5 x 73.5 x 4.00

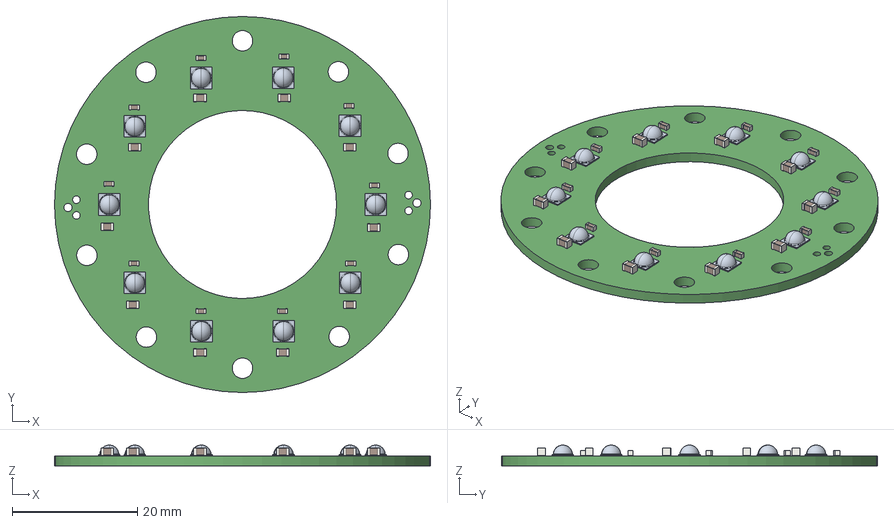
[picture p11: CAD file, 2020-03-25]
PCBs/Optics_holder/ring_illuminator.step
60.0 x 60.0 x 3.33 mm

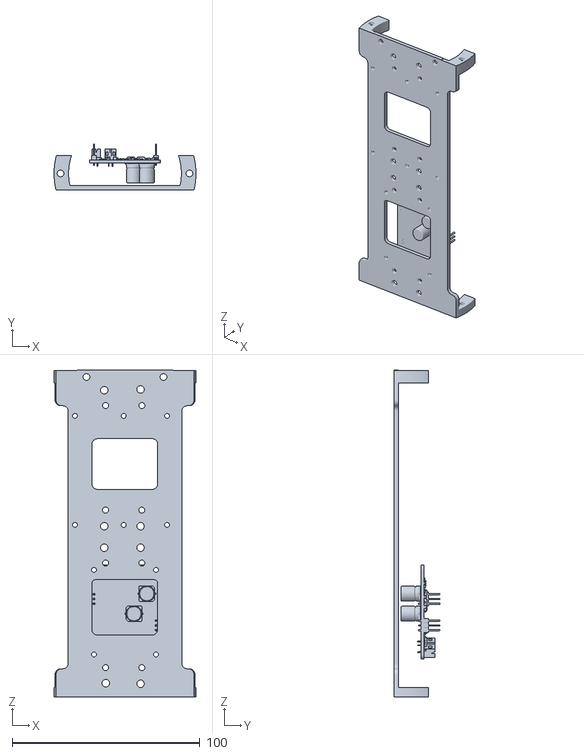
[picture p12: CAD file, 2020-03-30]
Mechanicals/PCB Tray.stl
75.5 x 24.4 x 174.0

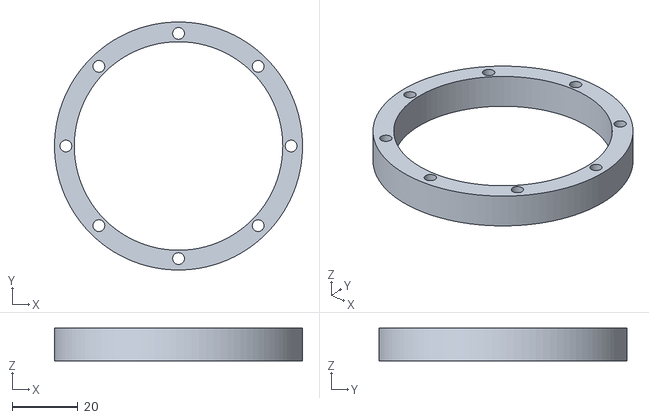
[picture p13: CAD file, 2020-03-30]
Mechanicals/Simple Tube Holder v3.stl
75.5 x 75.5 x 10.0

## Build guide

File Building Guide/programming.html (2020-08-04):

# IPAX Documentation

1. Home
2. Programming

# Programming

Last updated: March, 2020

## Overview

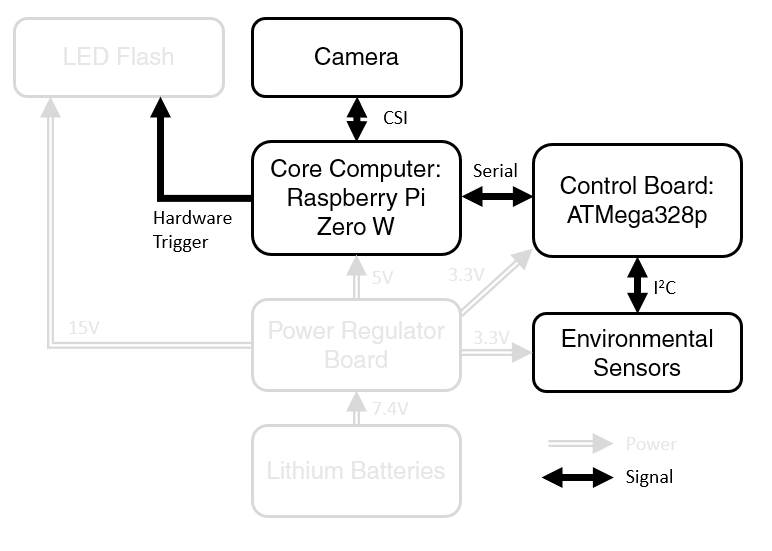
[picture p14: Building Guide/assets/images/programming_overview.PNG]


The programming for the IPAX is done on the control board and the Raspberry Pi. The control board is used to perform time keeping and interact with environmental sensor. It communicates with the Pi using Serial communication. The Pi is used to control camera for image acquisition and also to trigger the LED for flashing.

## Control Board Programming

### Arduino Setup

The control board is based on ATMega328p chip that is arduino-compatible. The guide will assume that users are familiar with Arduino platform for programming. There are many online tutorials on the basic of Arduino IDE, and users can download the platform directly from the official website (https://www.arduino.cc/).

This control board is modeled after Arduino Pro Mini 3.3V 8MHz, so make sure that the Arduino IDE is set accordingly. However, advanced users can set the chip to any configurations. We need to use Upload Using Programmer option when uploading the program with an ISP programmer.

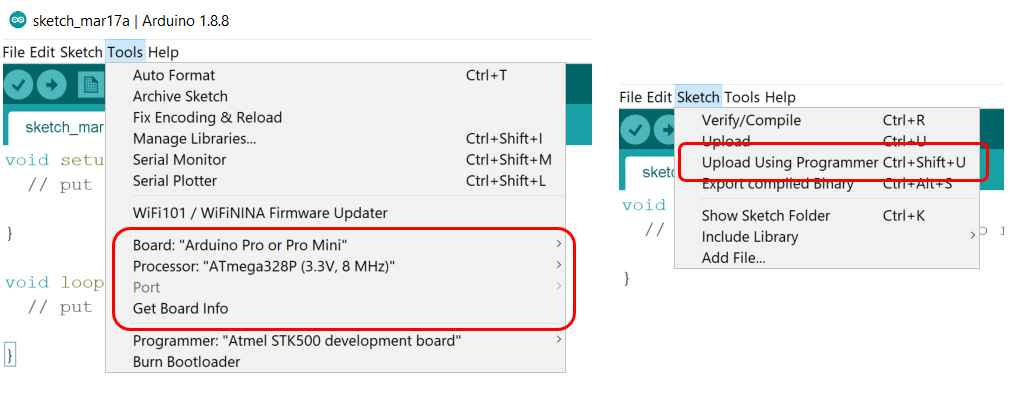
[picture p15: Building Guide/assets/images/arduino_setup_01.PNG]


To program, we need to have an ISP programmer, which is commercially available. We recommend using Pololu USB programmer (https://www.pololu.com/product/3172), though any ISP programmer will work well. There is also a UART header available on the control board for basic debugging through USB serial.

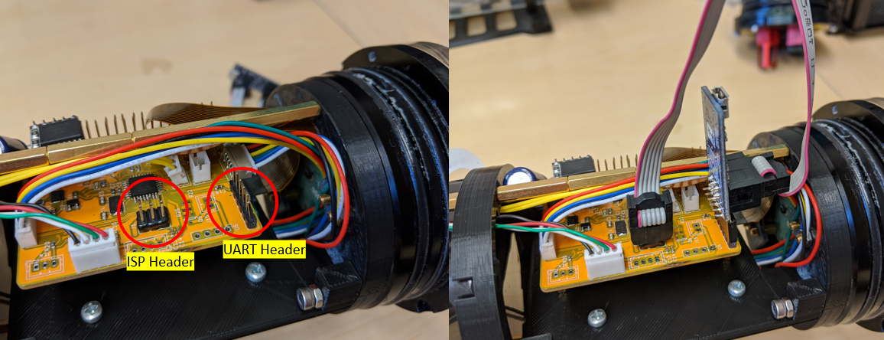
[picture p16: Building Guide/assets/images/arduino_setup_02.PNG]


### Arduino Programming

Two Arduino skecthes are available on the IPAX github page. There are a few Arduino libraries that we need to install for the code to properly work. Note that library #3-5 are optional and are only needed if there are actual sensors attached to the instrument.

1. DS3232RTC for real-time clock
2. LowPower for sleep mode
3. SparkFunBME280 for on-board BME280 sensor
4. MS5837 for Bluerobotics pressure sensor
5. TSYS01 for Bluerobotics temperature sensor

Upload the script to the control board and then check on the serial monitor. The output should be similar to what shown below. Make sure the baud rate is set to 9600. The output on the fourth line indicates the time of the system. If that number is incorrect, then we have to set the RTC.

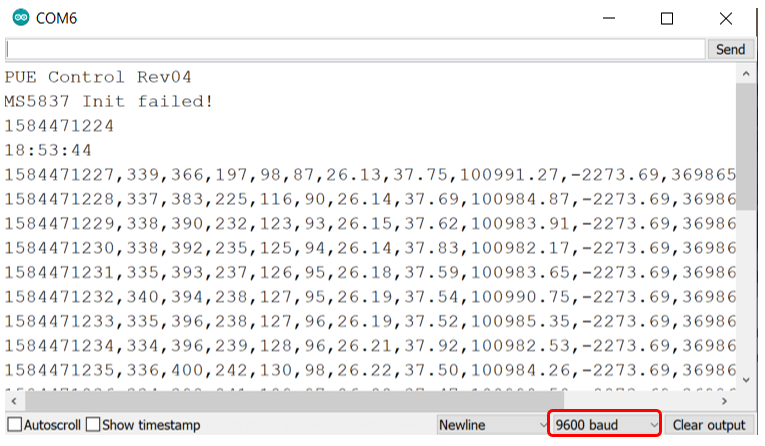
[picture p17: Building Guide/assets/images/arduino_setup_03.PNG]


## Raspberry Pi

### Raspberry Pi Setup

Again, users are assumed to be familiar with Raspberry Pi basic. There are many helpful tutorials available online to get started with Raspberry Pi, such as this official tutorial (https://projects.raspberrypi.org/en/projects/raspberry-pi-getting-started). However, apart from basic Raspberry Pi setup, there are a few setups we need that are specific to the IPAX.

#### General Configuration

The general configuration of the Pi is determined by the config.txt file located at /boot/config.txt. We need to enable all the necessary peripherals, including serial, camera, remote ssh and i2c. The config.txt file used in the IPAX is provided in the github page.

#### Flash Hardware Trigger

The general configuration of the Pi is determined by the config.txt file located at /boot/config.txt. We need to enable all the necessary peripherals, including serial, camera, remote ssh and i2c. The config.txt file used in the IPAX is provided in the github page.

Designed with by Xiaoying Riley (https://themes.3rdwavemedia.com/) for developers

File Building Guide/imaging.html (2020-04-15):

# IPAX Documentation

1. Home
2. Imaging

# Imaging

Last updated: April, 2020

## Illumination



IPAX uses ten CREE XPE2 LEDs for illumination. There are two main colors used for deployment, far red and white. Please consult the official datasheet linked below for full detail of the LEDs. The spectrum plots of XPE2 from the datasheet is shown here as a reference.

In addition to the LEDs, IPAX also uses secondary optics to focus light from the LEDs. The optics used here is Carclo 10.0mm Narrow Spot Lens (P/N 10412)

CREE XPE2 Datasheet (https://www.cree.com/led-components/media/documents/XLampXPE2.pdf) Carclo Lens Datasheet (http://www.carclo-optics.com/optic-10412?ledmanufacturer=cree&ledfamily=xp-e2)

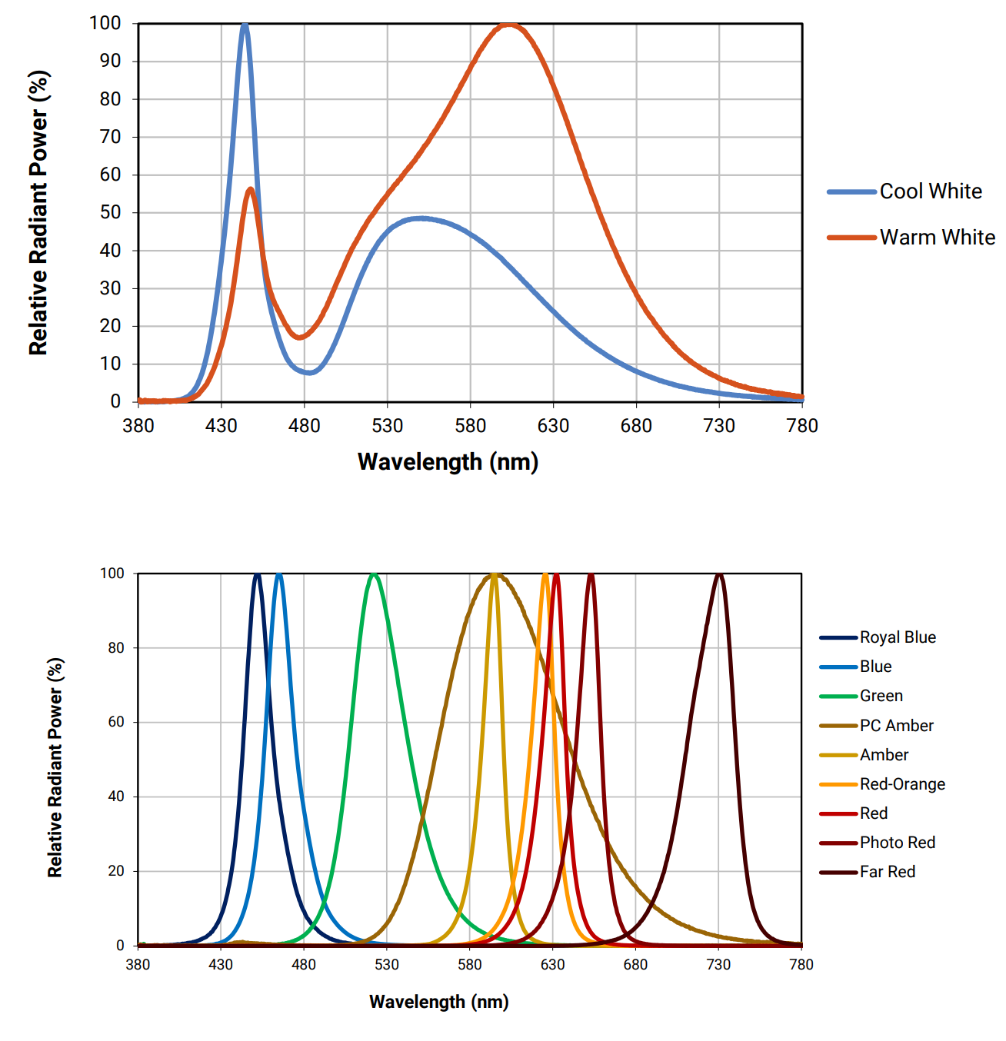
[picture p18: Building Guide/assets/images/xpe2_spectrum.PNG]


### LED Driver Circuit

The LED driver circuit is a part of the power control board. The schematic of the driver is shown below.

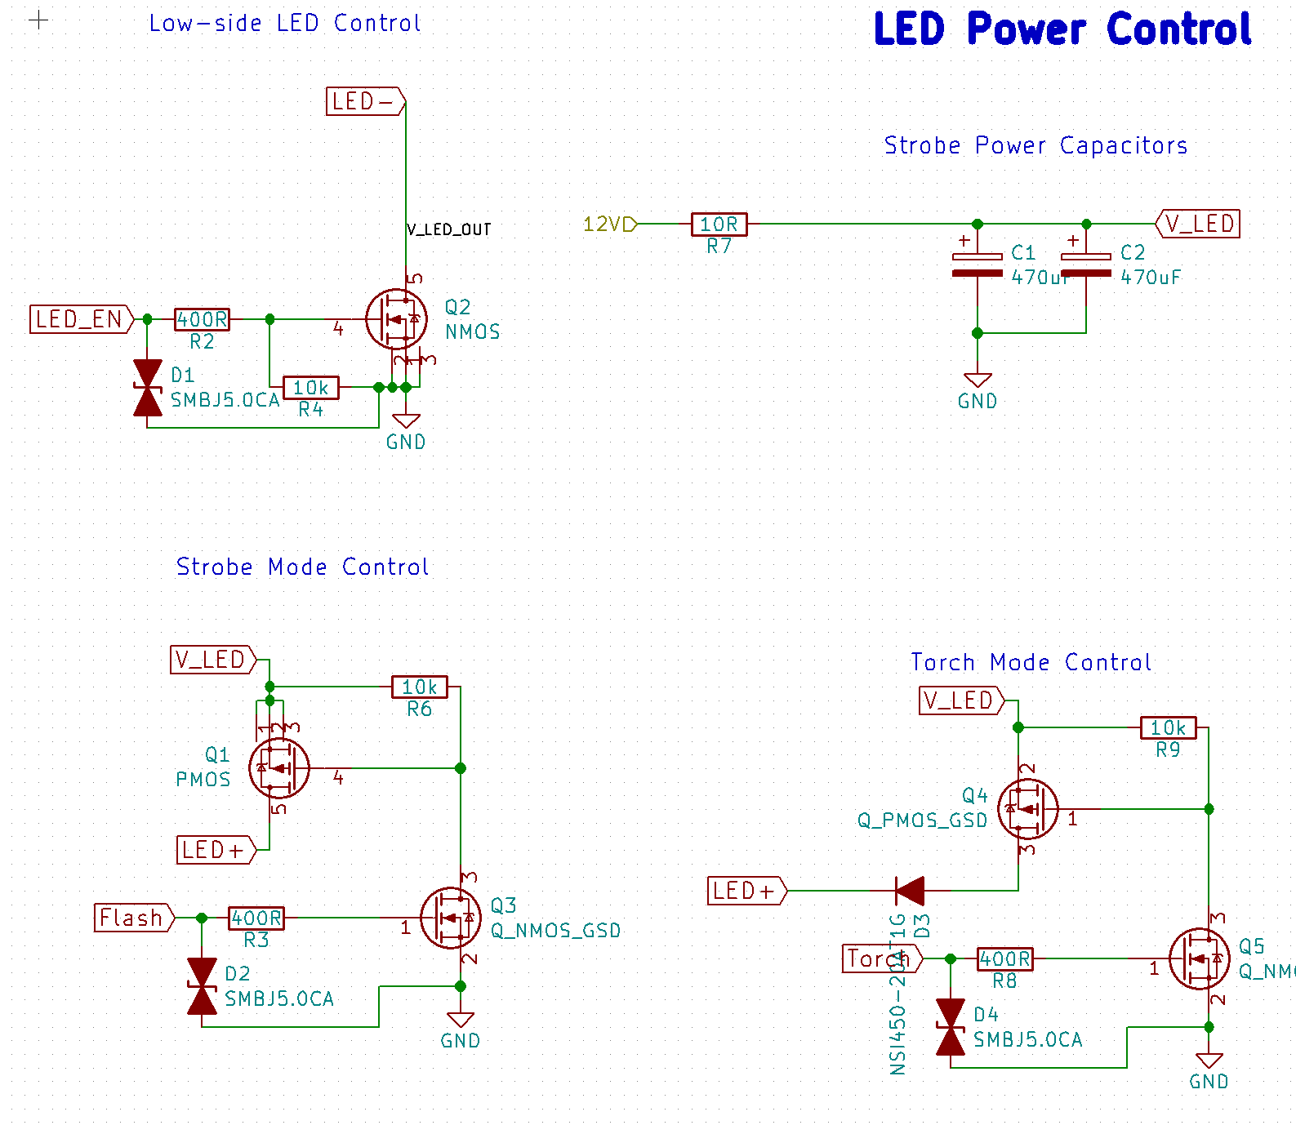
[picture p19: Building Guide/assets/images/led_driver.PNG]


There are two modes for illumination: (1) torch mode and (2) flash mode. Torch mode is simple control where the LEDs are always on or off without duty cycle. In this mode, the LEDs are driven by a constant current source diode (D3: NS1450 in this case). The LEDs stay pretty dim in this mode, so the board does not get overheat or consume too much power.

Flash mode is controlled by the triggering signal from IMX219. Once the trigger signal is high, the LEDs rapidly draw power from two large alumninum electrolytic capacitors (C1 and C2) to generate light. These capacitors help supply burst of current withouth straining the batteries and also generating more illumination in short period of time. Note that the Flash trigger should not be left ON for a prolonged period of time as it essentially shorts the LEDs drawing a lot of power and producing a lot of heat.

### LED Temperature

The PCB for the LED has aluminum substrate to help dissipate heat from each LED to the surrounding. The test shows that the temperature of the LED board is slightly elevated but is never high enough to cause trouble. The IPAX has a capability of adding an additional fan to help dissipate heat if the heat from the LEDs becomes a problem.

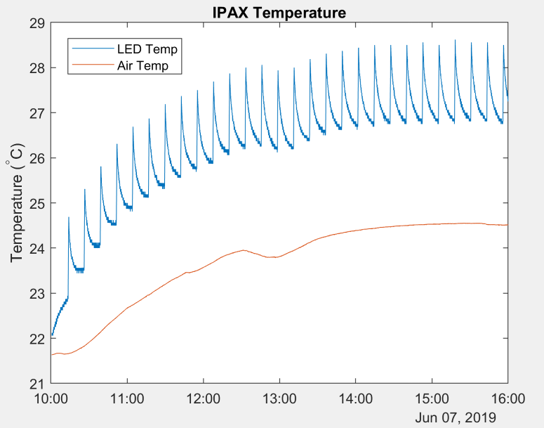
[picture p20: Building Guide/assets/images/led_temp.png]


## Pi Camera Flash

The RPi camera comes with an unconventional way of trigerring. It does not accept external hardware triggering, but it does output a trigerring signal for external flash. The method is outlined very well in the official documentaiton (https://picamera.readthedocs.io/en/release-1.13/recipes2.html#using-a-flash-with-the-camera). The setup can be done very easily by following the steps in the documentation. To make things easier, here is the dts-blob.bin files for IPAX. dt-blob.bin

### Flash Trigger Overview

The Pi camera sensor does not actually send out a trigger for external flash hardware. However, it sends out signal of when a frame capture begins and ends. For more detail, please visit the official documentaiton (https://picamera.readthedocs.io/en/latest/fov.html#theory-of-operation), especially, see Misconception #2. As a result, the flash trigger from the Pi camera is always at the start and end of the frame acquisition, resulting in a constant flash duration of fps/2. The brightness of the image is then controlled by the actual exposure time of the camera instead of the flash duration (unlike other microscopes controlled by Nvidia Jetson).

Here is the test of flash duration with different exposure time and fps setting. It can be seen that the exposure time of the camera does not affect the flash duration, but the fps setting does.

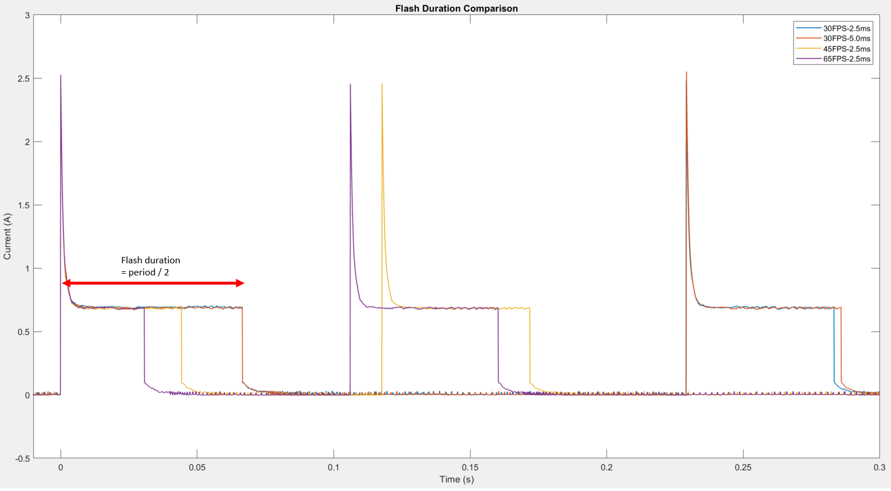
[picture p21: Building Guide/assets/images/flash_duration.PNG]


### Still Capture Flash

The flash mode is set by the parameter disable_camera_led in /boot/config.txt. Please consult this forum (https://www.raspberrypi.org/forums/viewtopic.php?t=190314) for the full description of values.

For still picture capturing, we use disable_camera_led=1, and then set camera.flash_mode = 'on' in the python implementation.

Using this flash mode, the camera will only flash twice for a single image acquisition. One before the actual acquisition and one during the acquisition. See the previous plot for detail.

### Video Flash

The flash mode for still images does not work on video capturing. The flash will simply not turn on at all when the camera is streaming the video. As a result, we need to work around this by setting disable_camera_led=3. With this setting, the flash is triggered every frame.

However, we cannot turn the flash off by this trigger alone when the camera is on. As a result, we need to add another flash controller. In IPAX, the flash trigger from the sensor control the high side of the LEDs, and another GPIO pin is used to control the low side of the LED to help conserve energy.

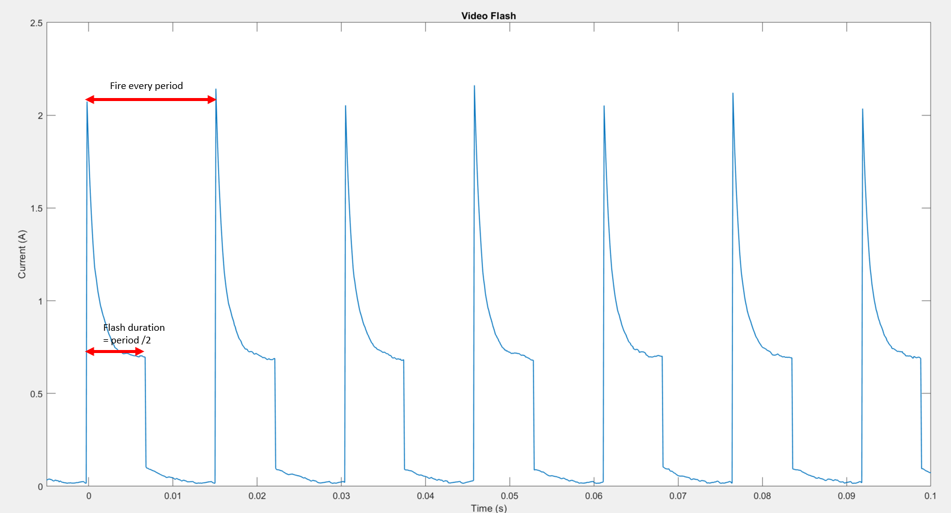
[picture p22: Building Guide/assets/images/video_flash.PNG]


Designed with by Xiaoying Riley (https://themes.3rdwavemedia.com/) for developers

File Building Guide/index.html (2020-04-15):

# IPAX Building Guide

### Overview

The overview of the IPAX and the build process

### Electronics

Circuit boards for IPAX

### Optics and Camera

LEDs, associated optics and camera

### Programming

Program the control board and Raspberry Pi

### Mechanical

3D printing and waterproof housing

### Miscellany

Troubleshooting and FAQs

Designed with by Xiaoying Riley (https://themes.3rdwavemedia.com/) for developers

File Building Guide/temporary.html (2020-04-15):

# IPAX Documentation

1. Home
2. Temporary

# Temporary

Last updated: April, 2020

## Under construction

Check back soon for updates on this section.

Designed with by Xiaoying Riley (https://themes.3rdwavemedia.com/) for developers

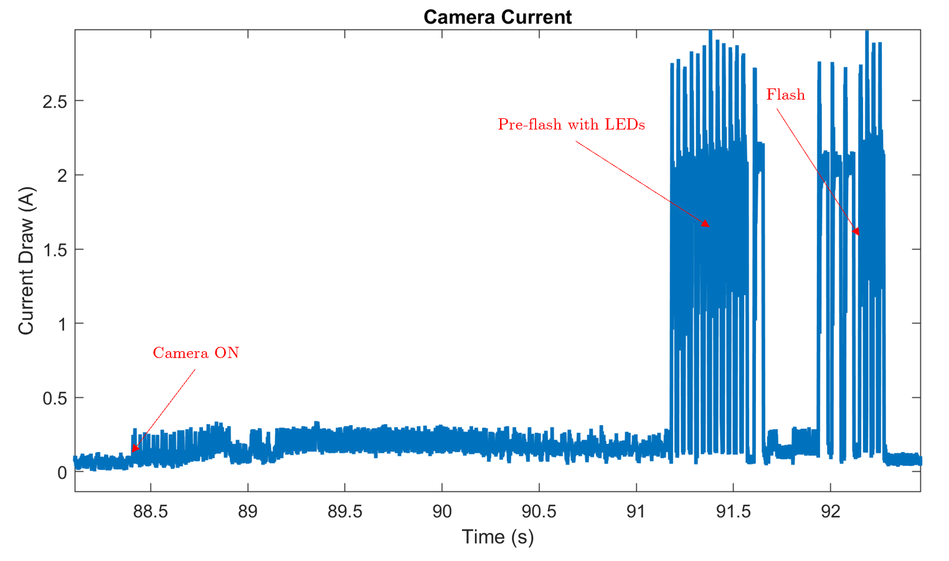
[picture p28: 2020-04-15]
Building Guide/assets/images/camera_current.PNG

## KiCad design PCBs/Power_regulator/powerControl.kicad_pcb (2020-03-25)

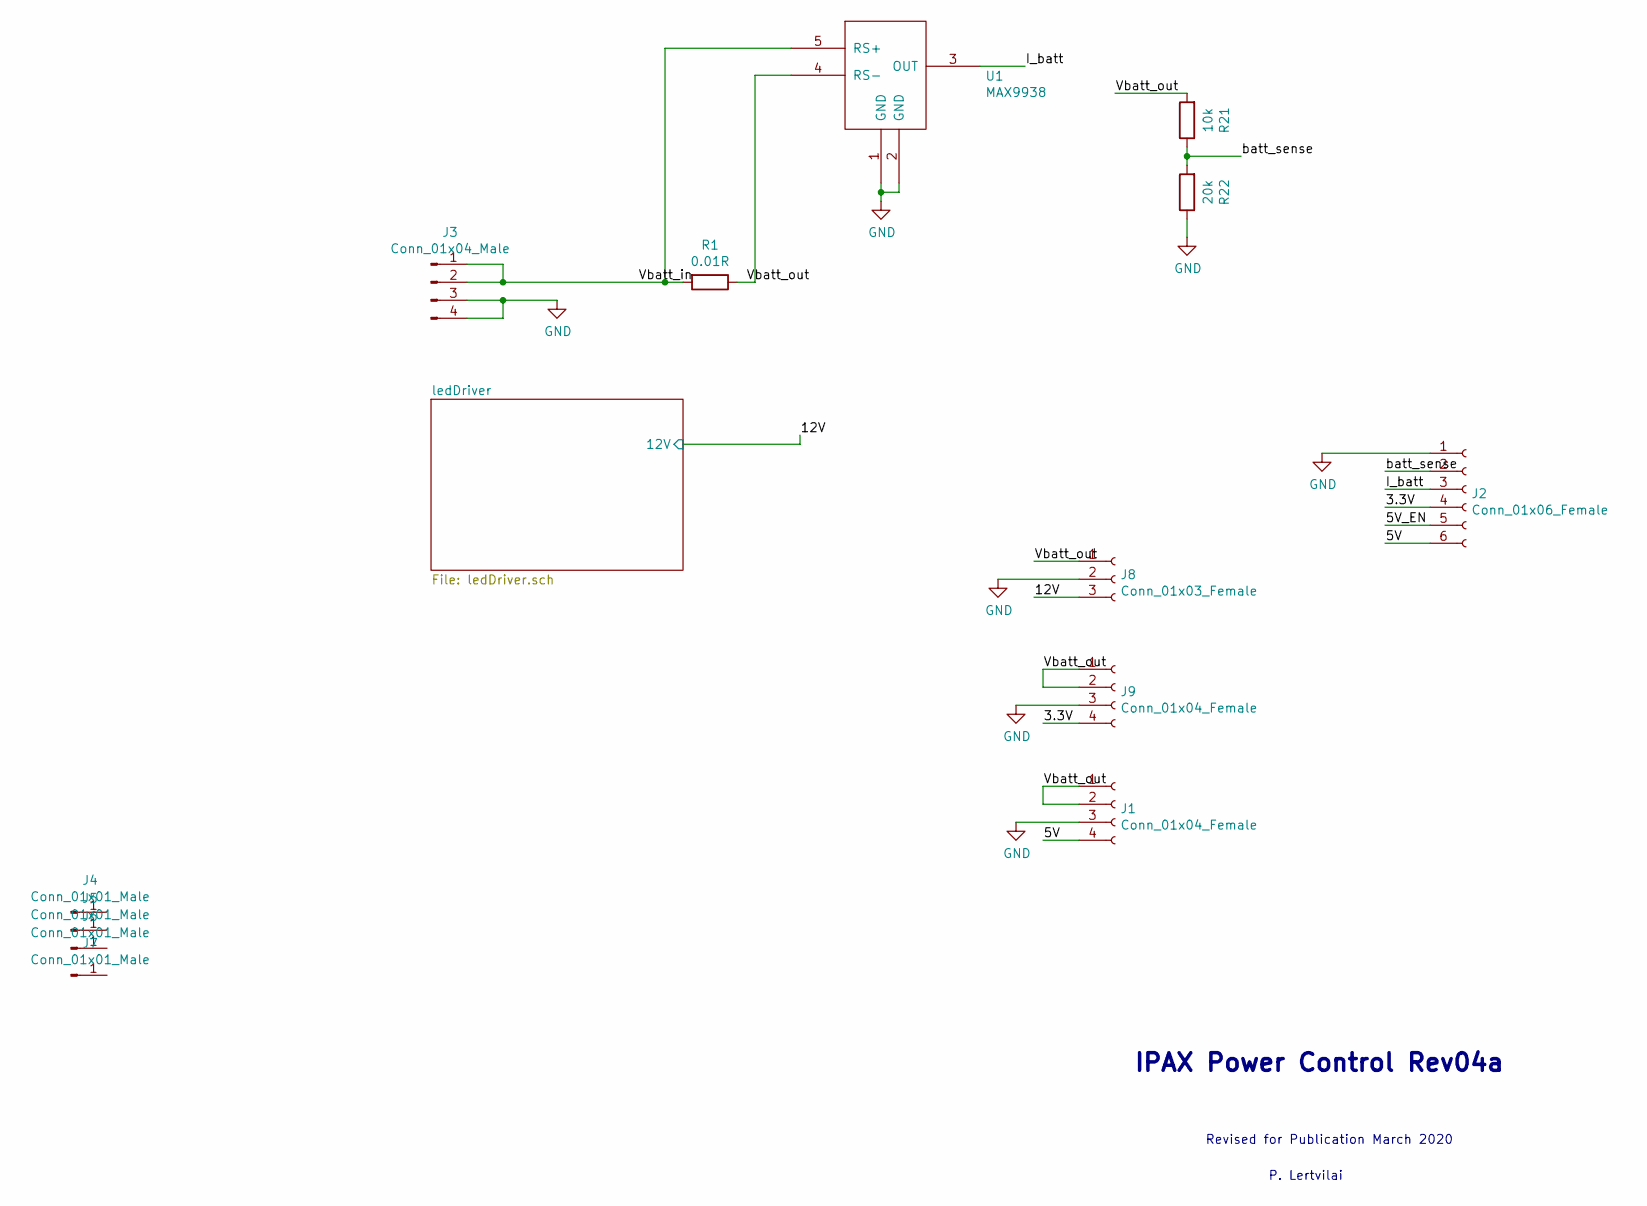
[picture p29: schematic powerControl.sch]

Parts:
J1, J9: Conn_01x04_Female; PinHeader_1x04_P2.54mm_Vertical
J2: Conn_01x06_Female; conn_1x06_1.5mm
J3: Conn_01x04_Male; Molex_Nano-Fit_105314-xx04_2x02_P2.50mm_Horizontal
J4, J5, J6, J7: Conn_01x01_Male; SCREW_4
J8: Conn_01x03_Female; PinHeader_1x03_P2.54mm_Vertical
R1: 0.01R; R_1206_3216Metric
R21: 10k; R_0603_1608Metric
R22: 20k; R_0603_1608Metric
U1: MAX9938; SOT-23-5

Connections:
/3.3V: J2.4, J9.4
/5V: J1.4, J2.6
/5V_EN: J2.5
/12V: J8.3; also elsewhere on the board
/I_batt: J2.3, U1.3 (OUT)
/Vbatt_in: J3.1, J3.2, R1.2, U1.5 (RS+)
/Vbatt_out: J1.1, J1.2, J8.1, J9.1, J9.2, R1.1, R21.2, U1.4 (RS-)
/batt_sense: J2.2, R21.1, R22.2
GND: J1.3, J2.1, J3.3, J3.4, J8.2, J9.3, R22.1, U1.1 (GND), U1.2 (GND); also elsewhere on the board

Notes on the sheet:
IPAX Power Control Rev04a
Revised for Publication March 2020
P. Lertvilai

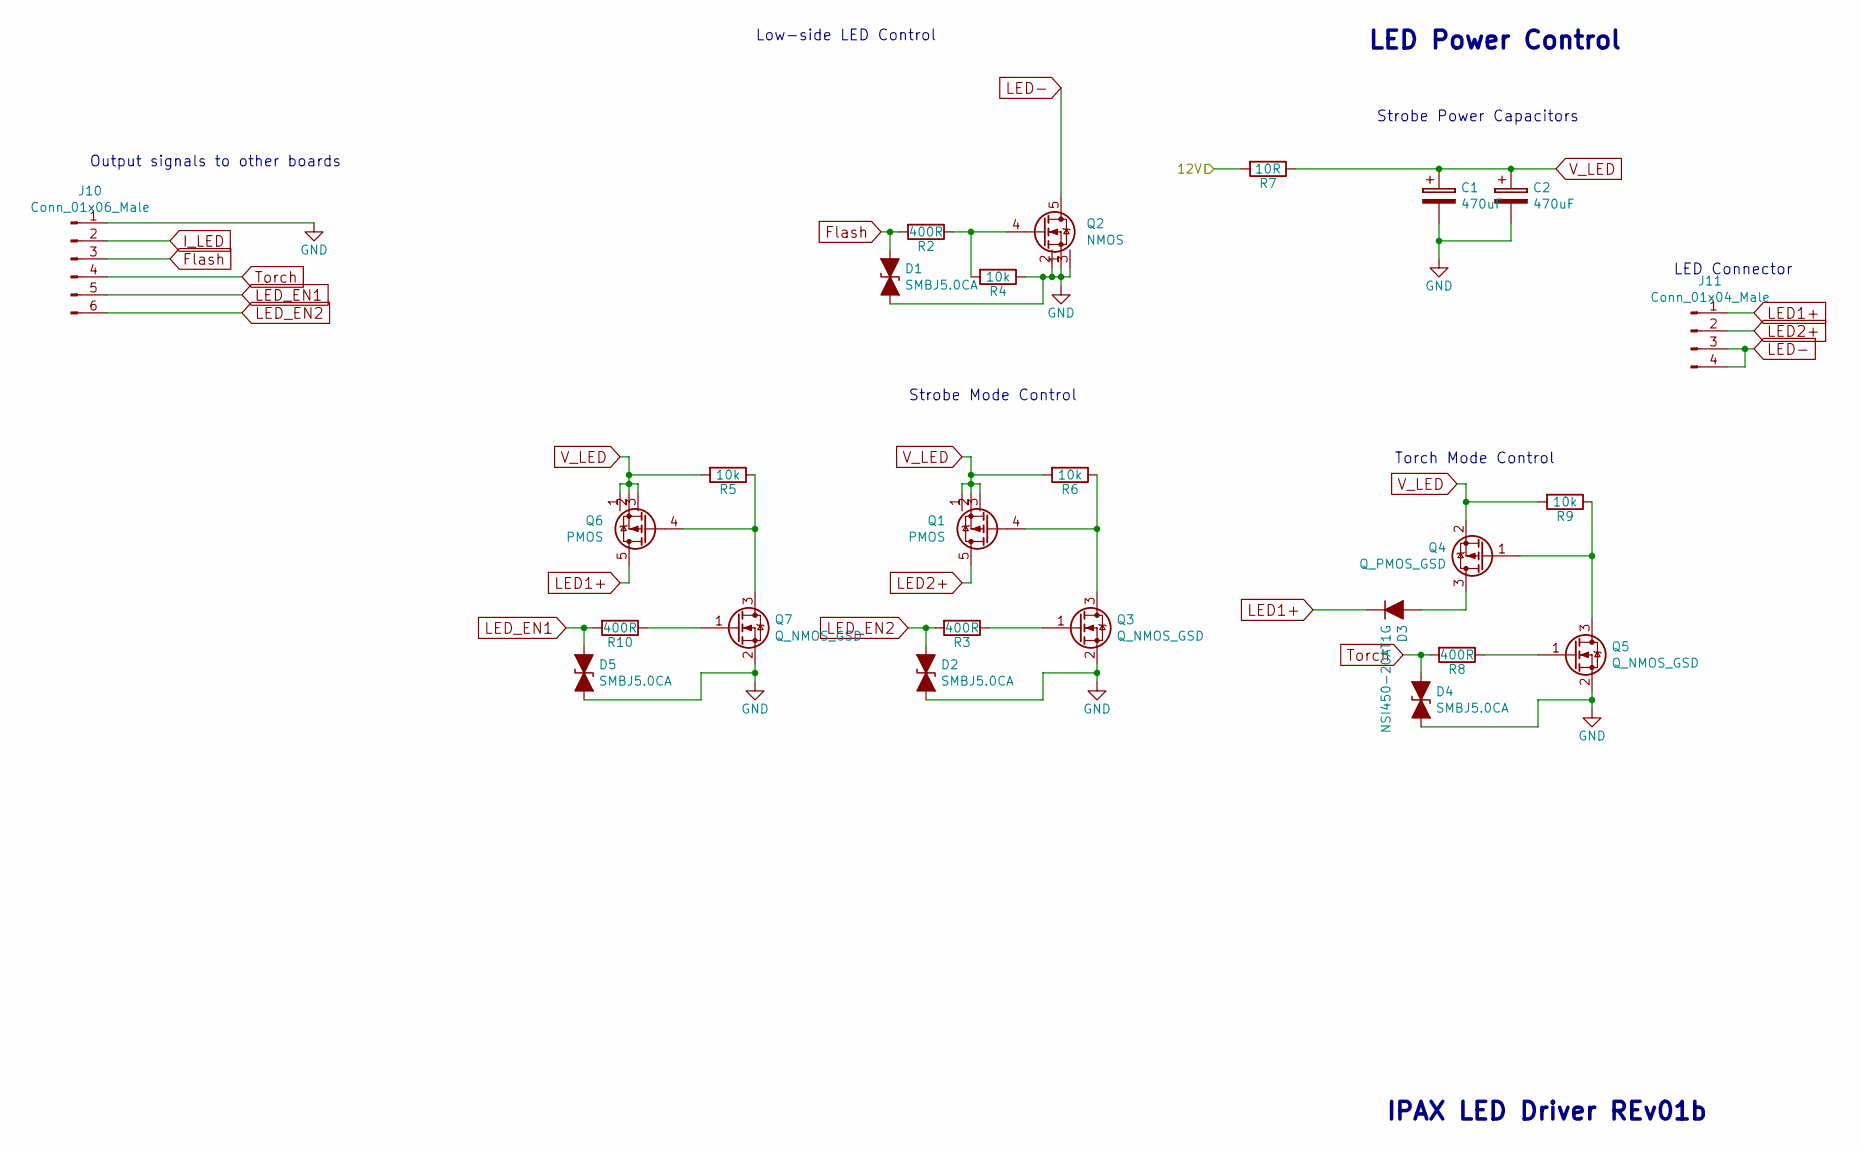
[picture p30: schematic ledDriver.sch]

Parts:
C1, C2: 470uF; CP_Radial_D10.0mm_P5.00mm
D1, D2, D4, D5: SMBJ5.0CA; DO-214AA
D3: NSI450-20AT1G; D_SOD-123
J10: Conn_01x06_Male; conn_1x06_1.5mm
J11: Conn_01x04_Male; Molex_Nano-Fit_105310-xx04_2x02_P2.50mm_Vertical
Q1, Q6: PMOS; Diodes_PowerDI3333-8
Q2: NMOS; Diodes_PowerDI3333-8
Q3, Q5, Q7: Q_NMOS_GSD; SOT-23
Q4: Q_PMOS_GSD; SOT-23
R2, R3, R8, R10: 400R; R_0603_1608Metric
R4, R5, R6, R9: 10k; R_0603_1608Metric
R7: 10R; R_1206_3216Metric

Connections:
/12V: R7.2; also elsewhere on the board
Flash: D1.1 (A1), J10.3, R2.2
GND: C1.2, C2.2, D1.2 (A2), D2.2 (A2), D4.2 (A2), D5.2 (A2), J10.1, Q2.1 (S), Q2.2 (S), Q2.3 (S), Q3.2 (S), Q5.2 (S), Q7.2 (S), R4.1; also elsewhere on the board
I_LED: J10.2
LED1+: D3.1 (K), J11.1, Q6.5 (D)
LED2+: J11.2, Q1.5 (D)
LED-: J11.3, J11.4, Q2.5 (D)
LED_EN1: D5.1 (A1), J10.5, R10.2
LED_EN2: D2.1 (A1), J10.6, R3.2
unnamed: D3.2 (A), Q4.3 (D)
unnamed: Q1.4 (G), Q3.3 (D), R6.1
unnamed: Q2.4 (G), R2.1, R4.2
unnamed: Q3.1 (G), R3.1
unnamed: Q4.1 (G), Q5.3 (D), R9.1
unnamed: Q5.1 (G), R8.1
unnamed: Q6.4 (G), Q7.3 (D), R5.1
unnamed: Q7.1 (G), R10.1
Torch: D4.1 (A1), J10.4, R8.2
V_LED: C1.1, C2.1, Q1.1 (S), Q1.2 (S), Q1.3 (S), Q4.2 (S), Q6.1 (S), Q6.2 (S), Q6.3 (S), R5.2, R6.2, R7.1, R9.2

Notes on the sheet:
IPAX LED Driver REv01b
Strobe Power Capacitors
Strobe Mode Control
LED Power Control
LED Connector
Torch Mode Control
Low-side LED Control
Output signals to other boards

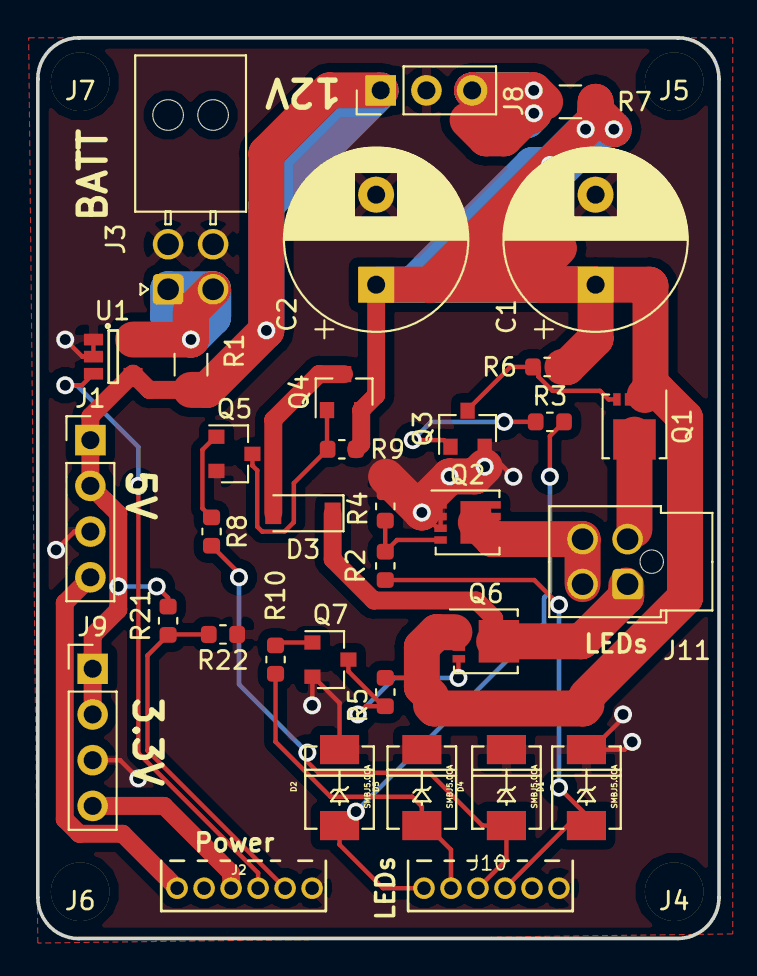
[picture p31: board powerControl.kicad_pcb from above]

Board: 2 copper layers, 37.8 x 50.0 mm, 38 parts (0 on the bottom side), 24 nets.

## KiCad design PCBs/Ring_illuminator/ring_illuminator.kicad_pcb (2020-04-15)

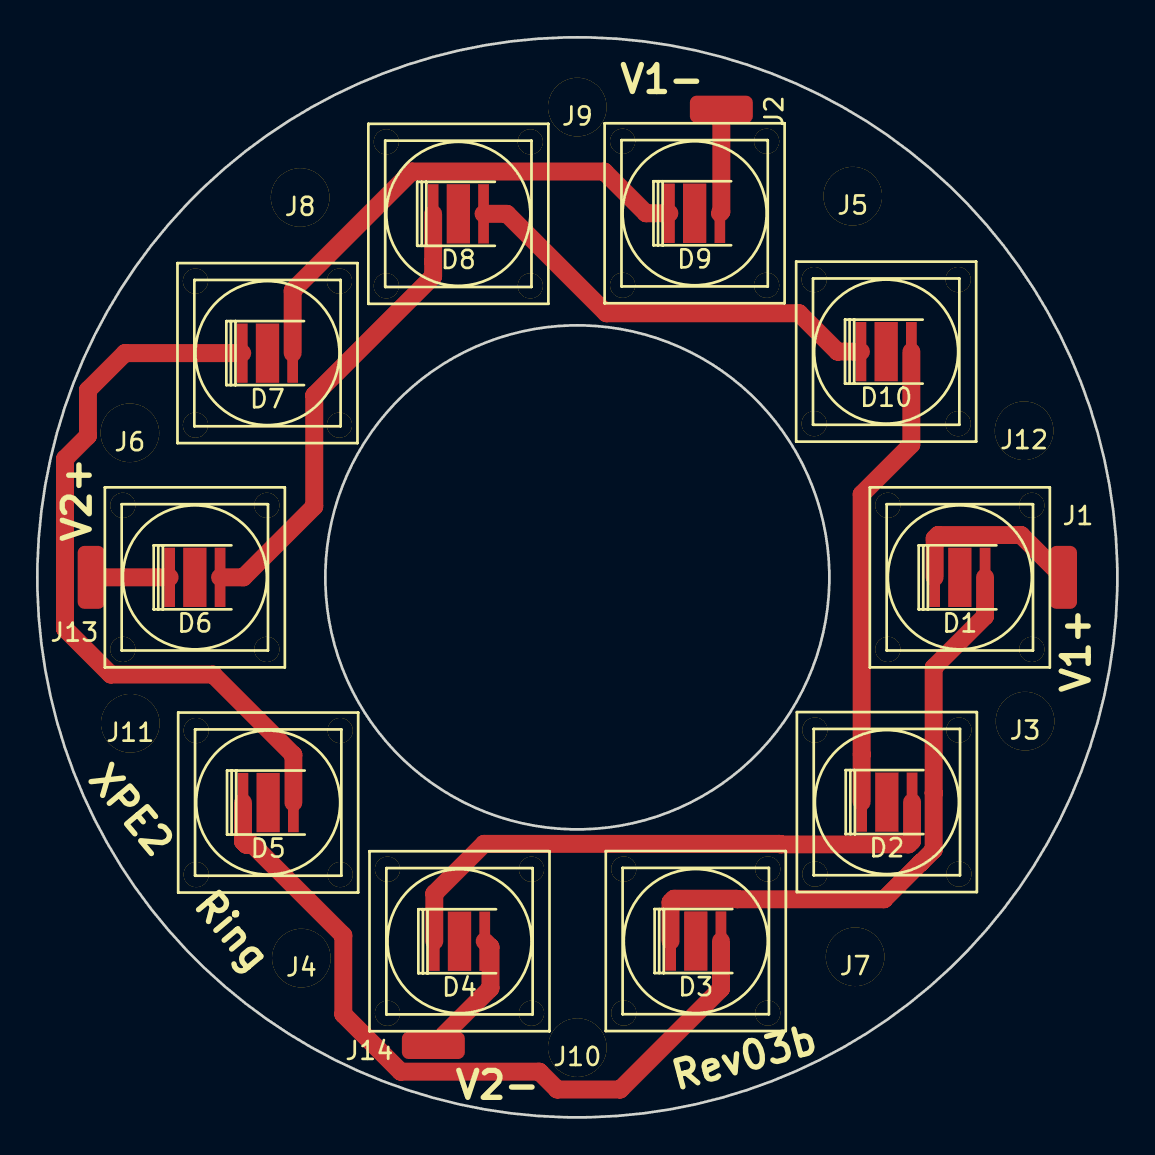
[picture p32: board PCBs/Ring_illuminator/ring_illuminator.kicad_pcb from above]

Board: 2 copper layers, 60.0 x 60.0 mm, 24 parts (0 on the bottom side), 12 nets.

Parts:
D1, D2, D3, D4, D5, D6, D7, D8, D9, D10: LED; CREE_XTE_Carclo_10mm
J1, J2, J13, J14: Conn_01x01_Female; large_smd_pad
J3, J4, J5, J6, J7, J8, J9, J10, J11, J12: Conn_01x01_Female; SCREW_4

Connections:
LED1+: D1.2, J1.1
LED1-: D9.1, J2.1
LED2+: D6.2, J13.1
LED2-: D4.1, J14.1
unnamed: D1.1, D3.2
unnamed: D2.1, D4.2
unnamed: D3.1, D5.2
unnamed: D5.1, D7.2
unnamed: D6.1, D8.2
unnamed: D7.1, D9.2
unnamed: D2.2, D10.1
unnamed: D8.1, D10.2

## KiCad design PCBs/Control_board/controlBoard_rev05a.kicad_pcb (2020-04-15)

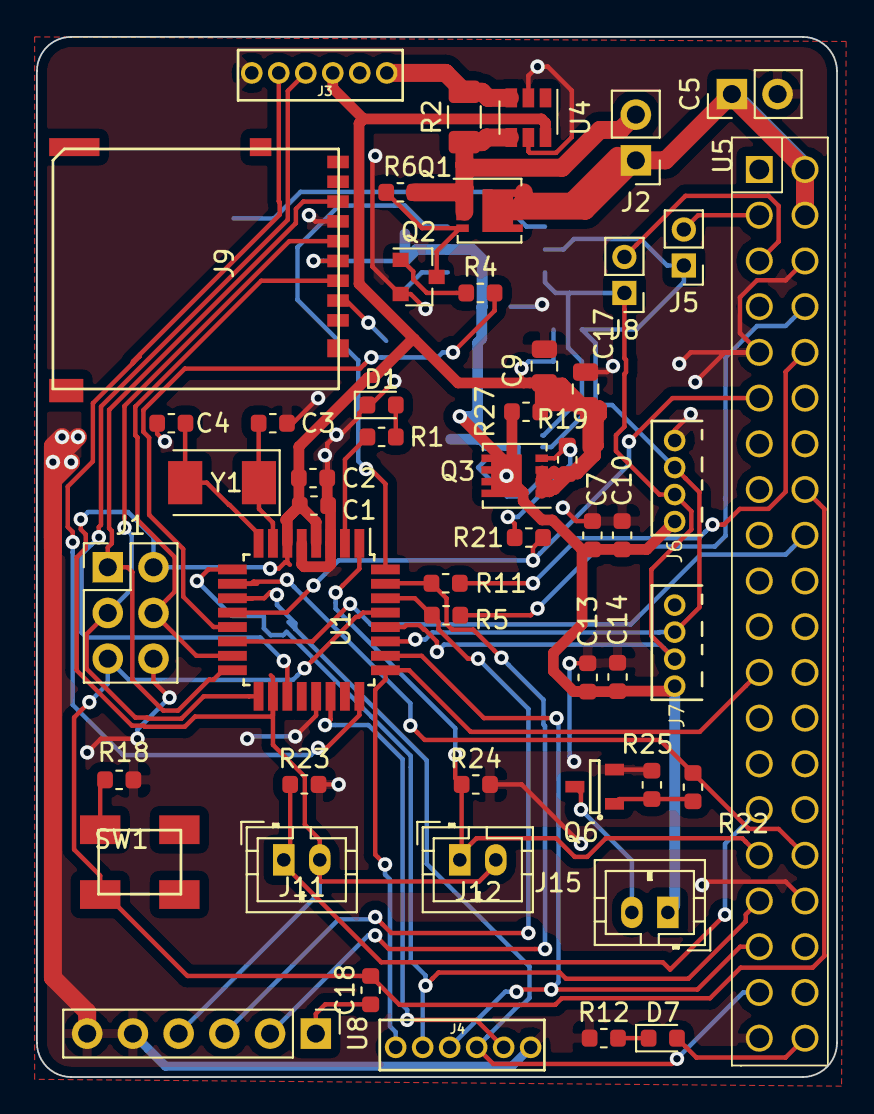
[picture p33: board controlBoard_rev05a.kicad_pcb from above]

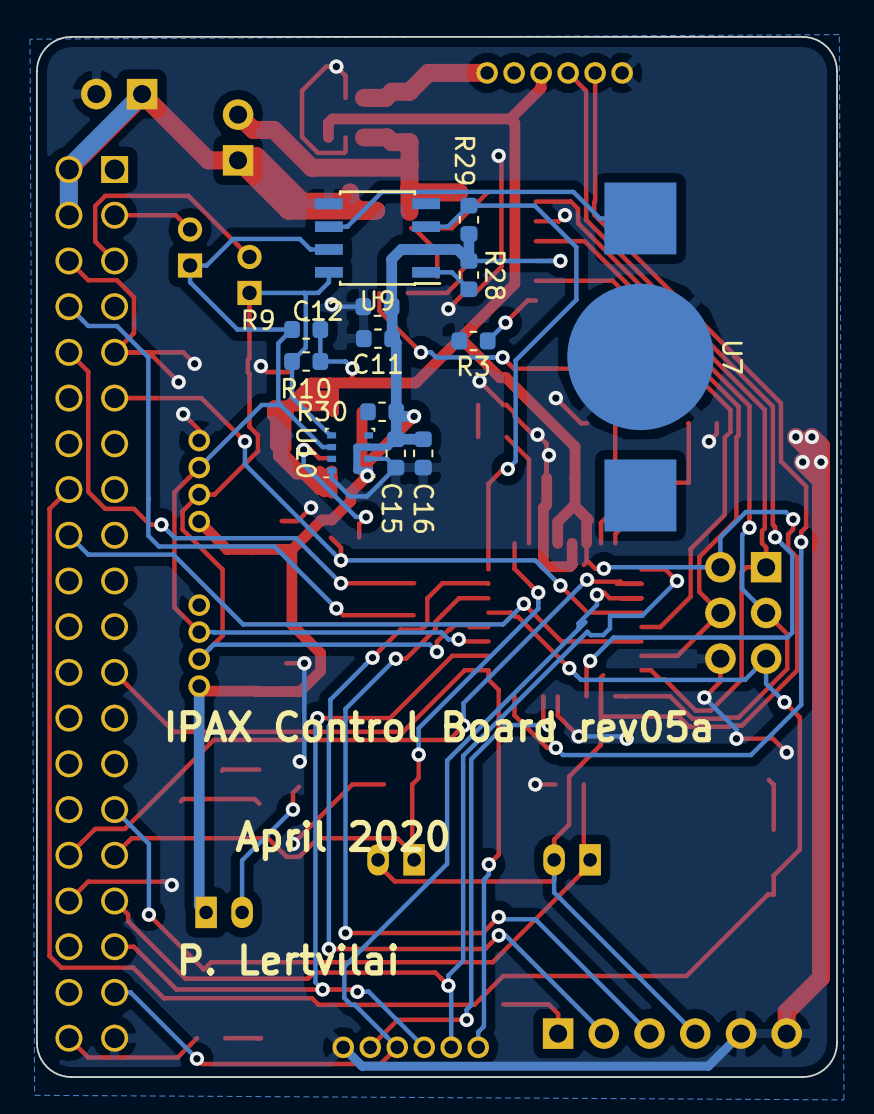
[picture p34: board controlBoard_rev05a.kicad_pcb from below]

Board: 2 copper layers, 44.5 x 57.8 mm, 64 parts (13 on the bottom side), 49 nets.

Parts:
C1, C10, C12, C14, C16: 1uF; C_0603_1608Metric
C2, C18: 0.1uF; C_0603_1608Metric
C3, C4: 22pF; C_0603_1608Metric
C5: CP; PinHeader_1x02_P2.54mm_Vertical
C7, C11, C13, C15: 10nF; C_0603_1608Metric
C9, C17: 22uF; C_0805_2012Metric
D1, D7: LED; LED_0603_1608Metric
J1: Conn_02x03_Odd_Even; PinHeader_2x03_P2.54mm_Vertical
J2: Conn_01x02_Male; PinHeader_1x02_P2.54mm_Vertical
J3, J4: Conn_01x06_Male; conn_1x06_1.5mm
J5, J8: Conn_01x02_Female; PinHeader_1x02_P2.00mm_Vertical
J6, J7: Conn_01x04_Male; conn_1x04_1.5mm
J9: Micro_SD_Card; DM3AT_microSD
J11, J12, J15: Conn_01x02_Male; JST_PH_B2B-PH-K_1x02_P2.00mm_Vertical
Q1, Q3: PMOS; Diodes_PowerDI3333-8
Q2: Q_NMOS_GSD; SOT-23
Q6: Q_NMOS_GSD; SOT-23-3
R1, R4, R5, R11, R12: 400R; R_0603_1608Metric
R2: 0.01R; R_1206_3216Metric
R3, R6, R9, R10, R18, R19, R23, R24, R25, R28, R29, R30: 10k; R_0603_1608Metric
R21, R22: 500R; R_0603_1608Metric
R27: jumper; R_0603_1608Metric
SW1: SW_DPST; SMD_pushbutton
U1: ATmega328P-AU; TQFP-32_7x7mm_P0.8mm
U4: INA181; SOT-23-6
U5: Pi_Header; RPi_Cobbler
U7: coin_cell; BK870_CR1025holder
U8: FTDI_Basic; PinHeader_1x06_P2.54mm_Vertical
U9: DS3231MZ; SOIC-8_3.9x4.9mm_P1.27mm
U10: BME280; Bosch_LGA-8_2.5x2.5mm_P0.65mm_ClockwisePinNumbering
Y1: Crystal; Crystal_SMD_Abracon_ABM3-2Pin_5.0x3.2mm

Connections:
3.3V_ARD: C1.1, C2.1, C9.1, C17.1, J1.2, J3.4, J11.2, J12.2, Q3.1, Q3.2, Q3.3, R9.1, R10.1, R19.2, R27.2, U1.4, U1.6, U1.18, U4.6, U8.4
3.3V_CTL: R21.1, U1.12, U5.6
3.3V_out: C7.1, C10.1, C11.1, C12.1, C13.1, C14.1, C15.1, C16.1, J6.1, J7.1, J9.4, J15.1, Q3.5, R27.1, R28.1, R29.1, R30.1, U9.2, U10.6, U10.8
5V: J2.2, Q1.1, Q1.2, Q1.3, R2.1, R6.2, U4.4
/Pi_SCL: J8.2, U5.3
/Pi_SDA: J5.2, U5.2
/powerControl/5V_IN: J3.6, R2.2, U4.3
CRYSTAL1: C3.1, U1.7, Y1.1
CRYSTAL2: C4.1, U1.8, Y1.2
CS: J9.2, R3.1
FAN_CTL: R22.2, U1.10, U5.25
Flash: J4.3, U1.11, U5.19
GND: C1.2, C2.2, C3.2, C4.2, C5.2, C7.2, C9.2, C10.2, C11.2, C12.2, C13.2, C14.2, C15.2, C16.2, C17.2, D1.1, J1.6, J3.1, J4.1, J6.4, J7.4, J9.6, Q2.2, Q6.2, R3.2, R12.1, R18.2, R23.2, R24.2, R25.1, U1.3, U1.5, U1.21, U4.2, U4.5, U5.5, U5.20, U5.24, U5.38, U7.1, U8.5, U8.6, U9.5, U10.1, U10.7
I_BATT: J3.3, U1.19
I_LED: J4.2, U1.22
LED_EN: J4.5, U1.9, U5.17
LED_EN2: J4.6, U1.25, U5.12
MISO: J1.1, J9.7, U1.16
MOSI: J1.4, J9.3, U1.15
unnamed: C18.1, U8.1
unnamed: D1.2, R1.1
unnamed: D7.1, R12.2
unnamed: D7.2, U5.21
unnamed: J15.2, Q6.3
unnamed: Q1.4, Q2.3, R6.1
unnamed: Q2.1, R4.1
unnamed: Q3.4, R19.1, R21.2
unnamed: Q6.1, R22.1, R25.2
unnamed: R1.2, U1.2
unnamed: R5.2, U5.37
unnamed: R11.2, U5.36
unnamed: R18.1, SW1.3
unnamed: R28.2, U9.1
unnamed: R30.2, U10.5
unnamed: U7.3, U9.6
PI_CTL: R4.2, U1.13
PI_SIG: U1.14, U5.32
PUSH: J11.1, R23.1, U5.15
PUSH2: J12.1, R24.1, U1.1, U5.16
RST: C18.2, J1.5, SW1.4, U1.29, U5.33
RXD: R5.1, U1.30, U8.3
SCK: J1.3, J9.5, U1.17
SCL: J6.2, J7.2, J8.1, R10.2, U1.28, U9.8, U10.4
SDA: J5.1, J6.3, J7.3, R9.2, U1.27, U9.7, U10.3
TXD: R11.1, U1.31, U8.2
Torch: J4.4, U1.26, U5.18
V_BATT: J3.2, U1.24
Vpi: C5.1, J2.1, Q1.5, U5.39, U5.40
alarm: R29.2, U1.32, U9.3

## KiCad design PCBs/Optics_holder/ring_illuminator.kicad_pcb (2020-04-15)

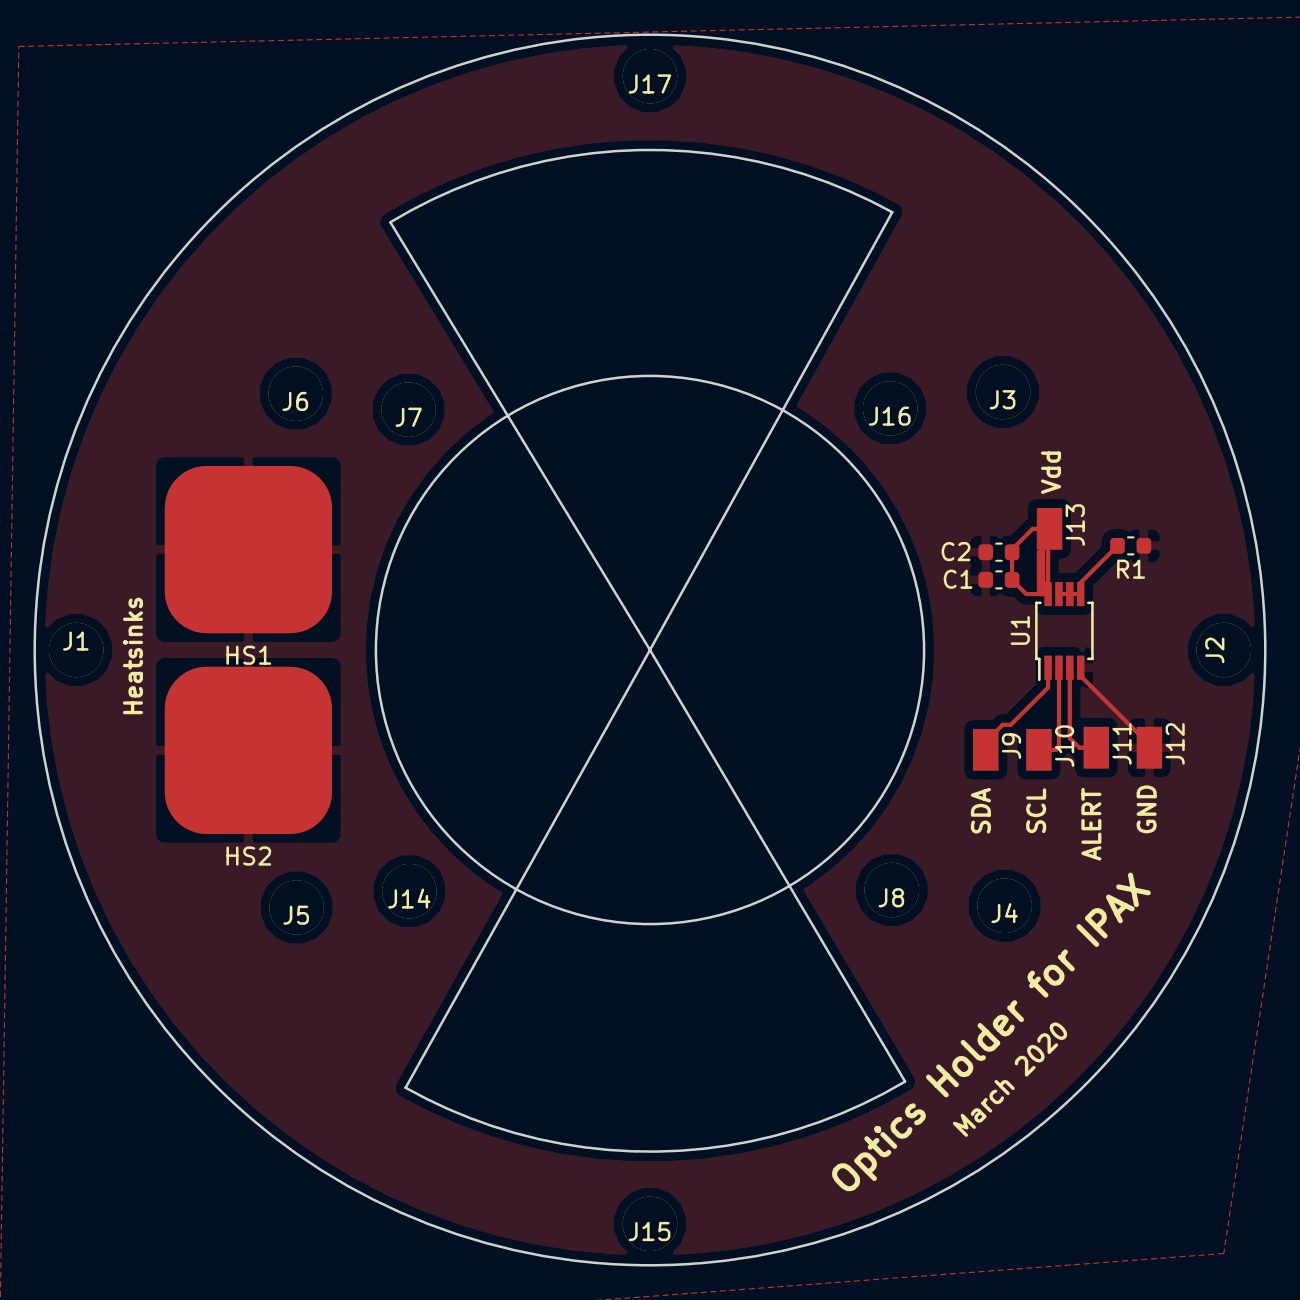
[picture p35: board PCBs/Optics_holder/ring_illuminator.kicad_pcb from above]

Board: 2 copper layers, 73.5 x 73.5 mm, 23 parts (0 on the bottom side), 6 nets.

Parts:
C1, C2: C; C_0603_1608Metric
HS1, HS2: Heatsink_Pad; HeatSink_10x10mm
J1, J2, J3, J4, J5, J6, J7, J8, J14, J15, J16, J17: Conn_01x01_Female; SCREW_4
J9, J10, J11, J12, J13: Conn_01x01_Male; small_smd_pad
R1: 10k; R_0603_1608Metric
U1: MCP9808; MSOP-8_3x3mm_P0.65mm

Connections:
/A0: R1.2, U1.5, U1.6, U1.7
/ALERT: J11.1, U1.3
/SCL: J10.1, U1.2
/SDA: J9.1, U1.1
/Vdd: C1.1, C2.1, J13.1, U1.8
GND: C1.2, C2.2, HS1.1, HS2.1, J12.1, R1.1, U1.4

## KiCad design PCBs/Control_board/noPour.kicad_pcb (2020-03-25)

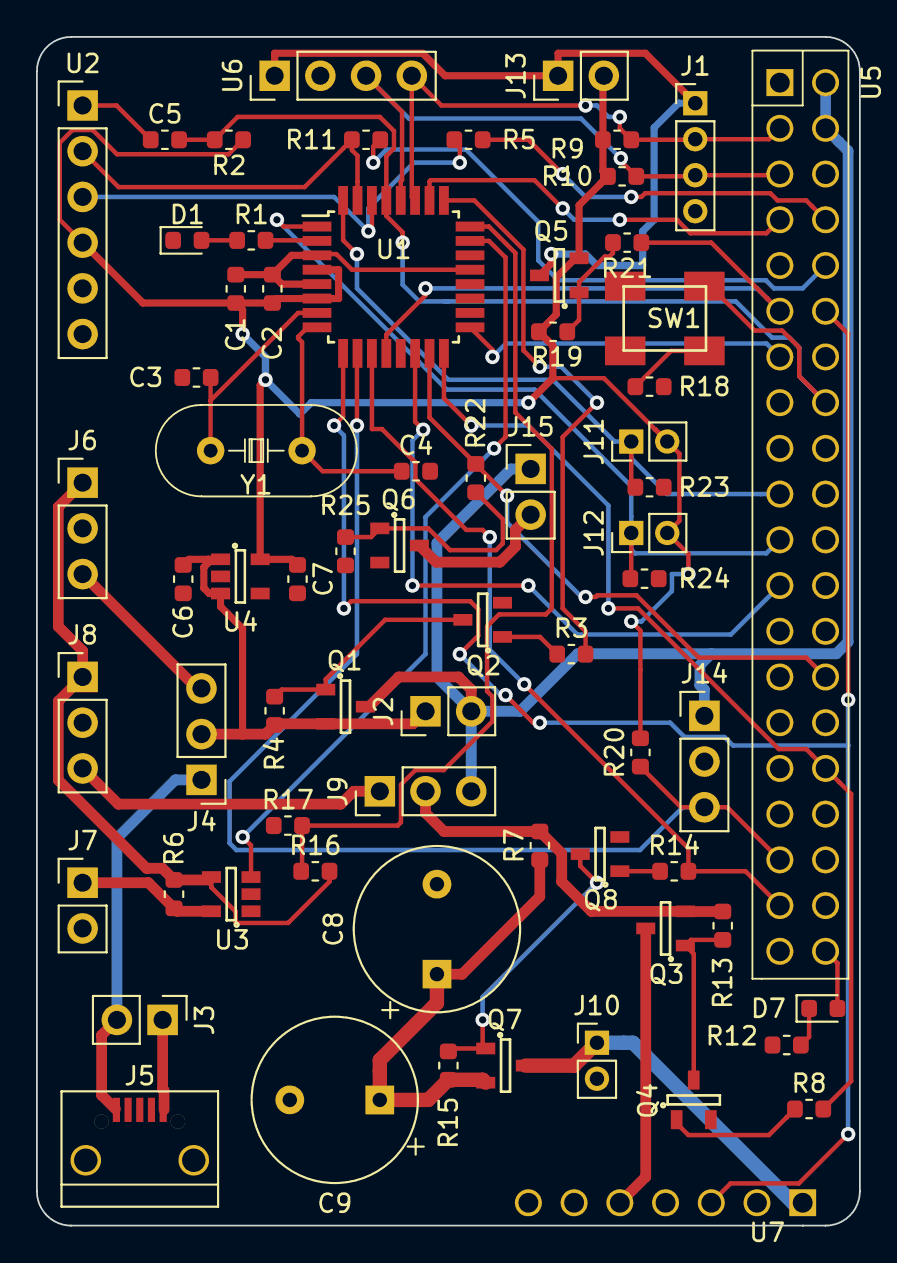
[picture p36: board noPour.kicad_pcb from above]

Board: 2 copper layers, 45.7 x 66.0 mm, 68 parts (0 on the bottom side), 52 nets.

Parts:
C1, C6, C7: 1uF; C_0603_1608Metric
C2, C5: 0.1uF; C_0603_1608Metric
C3, C4: 22pF; C_0603_1608Metric
C8, C9: 1000uF; CP_Radial_Tantal_D9.0mm_P5.00mm
D1, D7: LED; LED_0603_1608Metric
J1: Conn_01x04_Male; PinHeader_1x04_P2.00mm_Vertical
J2, J3, J7, J13, J15: Conn_01x02_Male; PinHeader_1x02_P2.54mm_Vertical
J4, J6, J8, J9, J14: Conn_01x03_Male; PinHeader_1x03_P2.54mm_Vertical
J5: USB_B_Micro; USB_Micro-B_eBay
J10, J11, J12: Conn_01x02_Male; PinHeader_1x02_P2.00mm_Vertical
Q1, Q3, Q5, Q7: Q_PMOS_GSD; SOT-23-3
Q2, Q4, Q6, Q8: Q_NMOS_GSD; SOT-23-3
R1, R3, R5, R8, R11, R12, R14: 400R; R_0603_1608Metric
R2, R4, R9, R10, R13, R15, R18, R23, R24: 10k; R_0603_1608Metric
R6: 0.01R; R_0603_1608Metric
R7, R16, R17, R19, R20, R21, R22, R25: R; R_0603_1608Metric
SW1: SW_DPST; SMD_pushbutton
U1: ATmega328P-AU; TQFP-32_7x7mm_P0.8mm
U2: FTDI_Basic; PinHeader_1x06_P2.54mm_Vertical
U3: MAX9938; SOT-23-5
U4: AP2112; SOT-23-5
U5: Pi_Header; RPi_Cobbler
U6: OLED_I2C; PinHeader_1x04_P2.54mm_Vertical
U7: LUXdriver; LUXdrive
Y1: Crystal; CRYSTAL_TH

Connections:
3.3V: C1.1, C2.1, C7.1, J11.2, J12.2, J13.2, Q5.2, R2.1, R9.1, R10.1, R19.2, R20.2, U1.4, U1.6, U2.4, U4.5
3.3V_CTL: R21.1, U1.12, U5.6
3.3V_out: J1.1, J13.1, Q5.3, U6.1
12V: J8.3, J9.1
Batt_sense: R16.1, R17.2, U1.24
CRYSTAL1: C3.1, U1.7, Y1.1
CRYSTAL2: C4.1, U1.8, Y1.2
CUR_OUT: U1.23, U3.3
FAN_CTL: R22.2, U1.15, U5.27
Flash: R14.2, U1.11, U5.19
GND: C1.2, C2.2, C3.2, C4.2, C6.2, C7.2, C8.2, C9.2, D1.1, J1.4, J3.1, J5.5, J6.2, J7.2, J8.2, J10.2, J14.2, Q2.2, Q4.2, Q6.2, Q8.2, R12.1, R17.1, R18.2, R23.2, R24.2, R25.1, U1.3, U1.5, U1.21, U2.5, U2.6, U3.1, U3.2, U4.2, U5.5, U5.20, U5.24, U5.38, U6.2, U7.2, U7.7
GPIO4: U1.26, U5.4
GPIO10: U1.14, U5.12
GPIO27: U1.17, U5.7
LED+: J10.1, Q7.3, U7.1
LED_CTL: R8.2, U1.16, U5.25
LEDdim: U1.9, U5.35, U7.3
LUXin: Q3.3, U7.5
unnamed: C5.1, U2.1
unnamed: D1.2, R1.1
unnamed: D7.1, R12.2
unnamed: D7.2, U5.21
unnamed: J15.2, Q6.3
unnamed: Q1.1, Q2.3, R4.1
unnamed: Q2.1, R3.1
unnamed: Q3.1, Q4.3, R13.1
unnamed: Q4.1, R8.1
unnamed: Q5.1, R19.1, R21.2
unnamed: Q6.1, R22.1, R25.2
unnamed: Q7.1, Q8.3, R15.1
unnamed: Q8.1, R14.1
unnamed: R1.2, U1.2
unnamed: R5.2, U5.37
unnamed: R11.2, U5.36
unnamed: R18.1, SW1.3
PI_CTL: R3.2, U1.25
PUSH: J11.1, R23.1, U1.32, U5.10
PUSH2: J12.1, R24.1, U1.1, U5.11
RST: C5.2, R2.2, SW1.4, U1.29, U5.33
RXD: R5.1, U1.30, U2.3
SCL: J1.3, R10.2, U1.28, U5.3, U6.3
SDA: J1.2, R9.2, U1.27, U5.2, U6.4
TXD: R11.1, U1.31, U2.2
V_FLASH: C8.1, C9.1, Q7.2, R7.1, R15.2
V_LED: J9.2, Q3.2, R7.2, R13.2
Vbatt: J6.1, J8.1, R6.1, R16.2, U3.4
Vbatt0: J7.1, R6.2, U3.5
Vbatt_out: J4.3, J6.3
Vhall: J14.3, R20.1, U1.10, U5.18
Vin: C6.1, J2.1, J4.2, Q1.2, R4.2, U4.1, U4.3
Vpi: J2.2, J9.3, J14.1, J15.1, Q1.3, U5.39, U5.40
Vusb: J3.2, J4.1, J5.1

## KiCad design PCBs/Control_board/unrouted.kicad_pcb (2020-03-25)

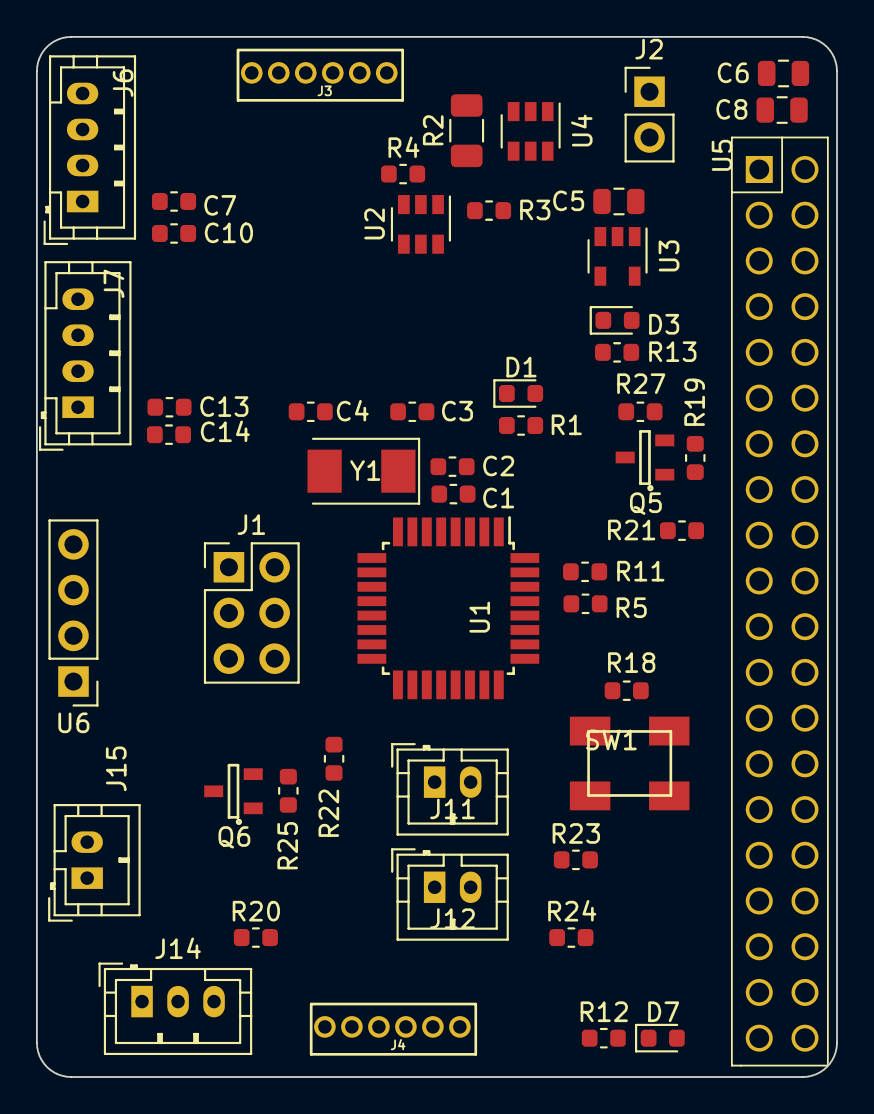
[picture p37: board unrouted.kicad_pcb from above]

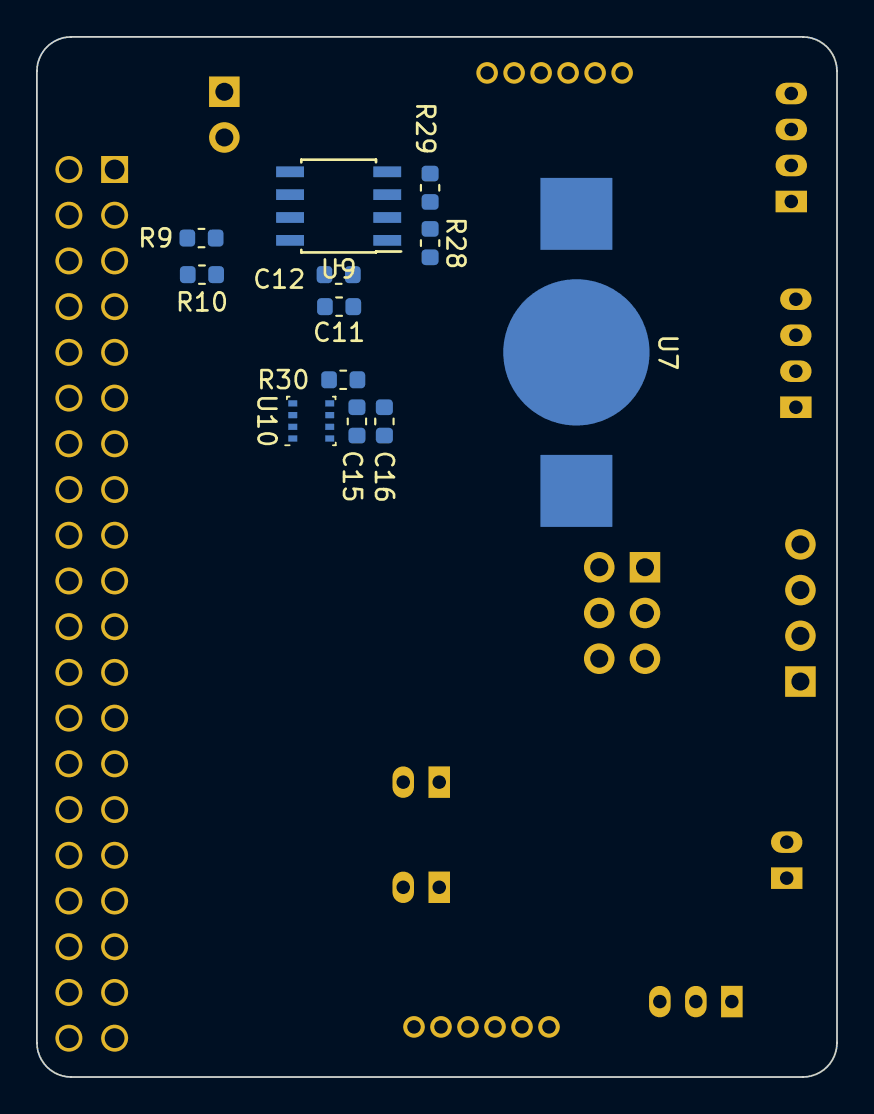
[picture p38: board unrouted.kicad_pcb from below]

Board: 2 copper layers, 44.5 x 57.8 mm, 63 parts (12 on the bottom side), 51 nets, no tracks yet.

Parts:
C1, C10, C12, C14, C16: 1uF; C_0603_1608Metric
C2: 0.1uF; C_0603_1608Metric
C3, C4: 22pF; C_0603_1608Metric
C5, C6, C8: 10uF; C_0805_2012Metric
C7, C11, C13, C15: 10nF; C_0603_1608Metric
D1, D7: LED; LED_0603_1608Metric
D3: RED; LED_0603_1608Metric
J1: Conn_02x03_Odd_Even; PinHeader_2x03_P2.54mm_Vertical
J2: Conn_01x02_Male; PinHeader_1x02_P2.54mm_Vertical
J3, J4: Conn_01x06_Male; conn_1x06_1.5mm
J6, J7: Conn_01x04_Male; JST_PH_B4B-PH-K_1x04_P2.00mm_Vertical
J11, J12, J15: Conn_01x02_Male; JST_PH_B2B-PH-K_1x02_P2.00mm_Vertical
J14: Conn_01x03_Male; JST_PH_B3B-PH-K_1x03_P2.00mm_Vertical
Q5: Q_PMOS_GSD; SOT-23-3
Q6: Q_NMOS_GSD; SOT-23-3
R1, R3, R5, R11, R12: 400R; R_0603_1608Metric
R2: 0.01R; R_1206_3216Metric
R4, R9, R10, R13, R18, R19, R20, R23, R24, R25, R28, R29, R30: 10k; R_0603_1608Metric
R21, R22: 500R; R_0603_1608Metric
R27: jumper; R_0603_1608Metric
SW1: SW_DPST; SMD_pushbutton
U1: ATmega328P-AU; TQFP-32_7x7mm_P0.8mm
U2: CEH2609_NP_Mosfet; SOT-23-6
U3: NCP361; SOT-23-5
U4: INA181; SOT-23-6
U5: Pi_Header; RPi_Cobbler
U6: OLED_I2C; PinHeader_1x04_P2.54mm_Vertical
U7: coin_cell; BK870_CR1025holder
U9: DS3231MZ; SOIC-8_3.9x4.9mm_P1.27mm
U10: BME280; Bosch_LGA-8_2.5x2.5mm_P0.65mm_ClockwisePinNumbering
Y1: Crystal; Crystal_SMD_Abracon_ABM3-2Pin_5.0x3.2mm

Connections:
3.3V: J11.2, J12.2, Q5.2, R9.1, R10.1, R19.2, R27.2, U5.1
3.3V_ARD: C1.1, C2.1, J1.2, J3.4, R20.2, U1.4, U1.6, U4.6
3.3V_CTL: R21.1, U1.12, U5.6
3.3V_out: C7.1, C10.1, C11.1, C12.1, C13.1, C14.1, C15.1, C16.1, J6.1, J7.1, Q5.3, R27.1, R28.1, R29.1, R30.1, U6.1, U9.2, U10.6, U10.8
5V: J2.2, J14.1, R2.1, R4.2, U2.2, U4.4
5V_EN: J3.5, U1.14
/powerControl/5V_IN: J3.6, R2.2, U4.3
/powerControl/5V_NPTC: C5.1, U2.4, U3.1
CRYSTAL1: C3.1, U1.7, Y1.1
CRYSTAL2: C4.1, U1.8, Y1.2
FAN_CTL: R22.2, U1.10, U5.27
Flash: J4.3, U1.11, U5.19
GND: C1.2, C2.2, C3.2, C4.2, C5.2, C6.2, C7.2, C8.2, C10.2, C11.2, C12.2, C13.2, C14.2, C15.2, C16.2, D1.1, J1.6, J3.1, J4.1, J6.4, J7.4, J14.2, Q6.2, R12.1, R18.2, R23.2, R24.2, R25.1, U1.3, U1.5, U1.21, U2.5, U3.2, U3.3, U4.2, U4.5, U5.5, U5.20, U5.24, U5.38, U6.2, U7.1, U9.5, U10.1, U10.7
I_BATT: J3.3, U1.23
I_LED: J4.2, U1.25
I_PI: U1.22, U4.1
LED_EN: J4.5, U1.9, U5.35
LED_SENSE: J4.6, U1.19
MISO: J1.1, U1.16
MOSI: J1.4, U1.15
unnamed: D1.2, R1.1
unnamed: D3.1, U3.4
unnamed: D3.2, R13.2
unnamed: D7.1, R12.2
unnamed: D7.2, U5.21
unnamed: J15.2, Q6.3
unnamed: Q5.1, R19.1, R21.2
unnamed: Q6.1, R22.1, R25.2
unnamed: R1.2, U1.2
unnamed: R3.1, U2.1
unnamed: R4.1, U2.3, U2.6
unnamed: R5.2, U5.37
unnamed: R11.2, U5.36
unnamed: R18.1, SW1.3
unnamed: R28.2, U9.1
unnamed: R30.2, U10.5
unnamed: U7.2, U7.3, U9.6
PI_CTL: R3.2, U1.13
PUSH: J11.1, R23.1, U5.10
PUSH2: J12.1, R24.1, U5.11
RST: J1.5, SW1.4, U1.29, U5.33
RXD: R5.1, U1.30
SCK: J1.3, U1.17
SCL: J6.2, J7.2, R10.2, U1.28, U5.3, U6.3, U9.8, U10.4
SDA: J6.3, J7.3, R9.2, U1.27, U5.2, U6.4, U9.7, U10.3
TXD: R11.1, U1.31
Torch: J4.4, U1.26
V_BATT: J3.2, U1.24
Vhall: J14.3, R20.1, U1.1, U5.18
Vpi: C6.1, C8.1, J2.1, J15.1, U3.5, U5.39, U5.40
alarm: R29.2, U1.32, U9.3

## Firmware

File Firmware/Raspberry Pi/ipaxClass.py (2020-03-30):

#!/usr/bin/python

# Library for IPAX
# P. Lertvilai
# Updated for Control Board Rev04 
# March 17, 2020

import io
import os
import time
#import cv2
import picamera
import numpy as np
import RPi.GPIO as GPIO
import datetime as dt

#------------------------pin assignment------------------------------#
#for IPAX, on-board led on pin 21 is controlled by connectArduino.py instead

button_pin = 10 #for push button
fan_pin = 27 #for fan control; not used in PUE v4.0
peri_pin = 17 #3.3V peripheral control; not useby Pi; Arduino controls all power management.
led_en_pin = 18 #low side control of LED
torch_pin = 19 # torch mode control for LED
# LED flash mode is pin 26; controlled directly through camera hardware
#hall_pin = 11 #for interrupt by Hall sensor; unused on Pi


class IPAX():

	def __init__(self):
		#GPIO
		self.buttonState = 0 #read button state at the beginning
		self.ledState = 0 #led pin state

		#file IO
		self.imageN = 30
		self.framerate = 50

		#get the next available still image number
		i = 0
		while os.path.exists("/home/pi/PUV/image/img%.5d_0.jpg" % i):
			i += 1
		self.imNum = i #use for still images

		#get the next available video number
		i = 0
		while os.path.exists("/home/pi/PUV/image/video%.5d.h264" % i):
			i += 1
		self.vidNum = i

		#camera
		self.camera = 0

		#time keeping
		self.time = time.time()
		self.recStart = 0
		self.recEnd = 0

		#others
		self.mode = 0

	def initialize(self):
		'''Initialize the GPIO pins of the instrument.
		Needs to be run at first for GPIO to function properly.
		Then, read the configuration file and set varaibles accordingly.'''
		GPIO.setmode(GPIO.BCM)
		GPIO.setup(button_pin, GPIO.IN)
		GPIO.setup(fan_pin, GPIO.OUT)
		GPIO.output(fan_pin, GPIO.LOW)
		GPIO.setup(led_en_pin, GPIO.OUT)
		GPIO.output(led_en_pin, GPIO.LOW)
		GPIO.setup(peri_pin, GPIO.OUT)
		GPIO.output(peri_pin, GPIO.HIGH) #3.3V CTL is active LOW 
		GPIO.setup(torch_pin, GPIO.OUT)

		self.buttonState = GPIO.input(button_pin)
		self.ledState = 0
		
		return True

	def ledON(self):
		'''Turn LED on.'''
		self.ledState = 1
		GPIO.output(led_en_pin, GPIO.HIGH)
		return True

	def ledOFF(self):
		'''Turn LED off.'''
		self.ledState = 0
		GPIO.output(led_en_pin, GPIO.LOW)
		return True

	def torchON(self):
		'''turn LED on torch mode.'''
		GPIO.output(torch_pin, GPIO.HIGH)
		return True

	def torchOFF(self):
		'''turn LED on torch mode.'''
		GPIO.output(torch_pin, GPIO.LOW)
		return True

	def cameraInit(self,shutter_speed=2500,resolution = (3280,2464),iso=200,awb_gains=(1.1,2.5)):
		'''Initialize camera.'''
		self.camera = picamera.PiCamera()
		self.camera.shutter_speed = shutter_speed #in microseconds
		self.camera.iso = iso
		self.camera.awb_mode = 'off'
		self.camera.awb_gains = awb_gains
		self.camera.resolution = resolution
		self.camera.flash_mode = 'on'
		self.camera.framerate = 30
		time.sleep(2) #wait for gain adjustment
		self.camera.exposure_mode = 'off'
		return True


	def cameraRelease(self):
		'''Release camera resources.'''
		print 'Closing camera'
		self.camera.close()
		#time.sleep(5)
		return True

	def oneShot(self,directory):
		'''Take one long exposure shot'''
		#self.ledON() #turn LED ON
		self.torchOFF() #make sure that torch mode is OFF
		#self.camera.capture(directory+'img%.5d_0.jpg'%(self.imNum))
		self.camera.capture(directory+'%d.jpg'%(time.time()))
		#self.ledOFF() #turn led off
		return True

	def videoRec(self,directory,recT):
		'''Take one long exposure shot'''
		#self.ledON() #turn LED ON
		self.torchOFF() #make sure that torch mode is OFF
		#self.camera.capture(directory+'img%.5d_0.jpg'%(self.imNum))
		self.camera.start_recording(directory+'%d.h264'%(time.time()))
		self.camera.wait_recording(recT)
		self.camera.stop_recording()
		#self.ledOFF() #turn led off
		return True

	def doubleShot(self,directory):
		'''Take two consecutive images. For use with PIV'''
		#self.ledON() #turn LED ON
		self.torchOFF() #make sure that torch mode is OFF
		self.camera.capture_sequence([directory+'img%.5d_0.jpg'%(self.imNum),directory+'img%.5d_1.jpg'%(self.imNum)])
		#self.ledOFF() #turn led off
		return True

	def recordInfo(self,directory,pressure,temp):
		'''Record image info to files.
		Mode == 0 -> video mode; else burst shot mode.'''
		file = open(directory+'stillAux.csv','a') 
		file.write('%.1f,%d,%.2f,%.2f\n'%(time.time(),self.imNum,pressure,temp))
		return True

	def incrementImNum(self):
		self.imNum = self.imNum+1

	def checkButtonStat(self):
		'''Check whether the button is released.
		3 is the default state where button is not pressed.
		1 is when button is kept pressed.
		4 button release
		2 button initial press'''
		buttonPress = GPIO.input(button_pin) #read button
		if buttonPress and self.buttonState: #if the button is pressed (from being pressed)
			self.buttonState = 1 #change button state
			return 1
		elif buttonPress and not self.buttonState: #if the button is pressed (from not being pressed)
			self.buttonState = 1
			return 2
		elif not buttonPress and not self.buttonState: #if the button is not pressed (from not being pressed)
			self.buttonState = 0
			return 3
		elif not buttonPress and self.buttonState: #if the button is not pressed (from being pressed)
			self.buttonState = 0
			return 4
		else:
			return 5

	def readButton(self):
		return GPIO.input(button_pin)

	def buttonCommand(self,timeOut=3):
		'''Accept command from one button.
		The timeout is in second and default to 3s.'''
		start = time.time()
		count = 0
		while(time.time()-start<timeOut):
			if self.checkButtonStat() == 2: #if button is pressed from not pressed
				count = count+1
				time.sleep(0.3) #for debouncing
			time.sleep(0.1) 
		return count

	def checkTime(self,second):
		'''check whether time has passed in second.'''
		if time.time()-self.time>second:
			self.time = time.time()
			return True
		else:
			return False

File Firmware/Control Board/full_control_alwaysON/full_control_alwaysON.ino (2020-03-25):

/* IPAX
 *  Arduino Script for testing and 
 *  for keeping the system ON all the time without low power mode
 *  March, 2020
 *  P. Lertvilai
 */

#include <DS3232RTC.h> //for DS3231 RTC
#include "LowPower.h" // for low power mode

/******MS5837 Pressure Sensor*************/
#include <Wire.h>
#include "MS5837.h"
MS5837 sensor;
/******BME280 Environmental Sensor*************/
#include <SparkFunBME280.h>
BME280 bme280Sensor; // Global temp/humidity/pressure sensor object

/**********TYSY01 Temperature Sensor***************/
#include "TSYS01.h"
#include <Wire.h>
TSYS01 temp_sensor;

/**********MCP9808 Temperature Sensor***************/
#include "Adafruit_MCP9808.h"
// Create the MCP9808 temperature sensor object
Adafruit_MCP9808 tempsensor = Adafruit_MCP9808();


//analog pin assigments
const int ibatt_pin = A0;
const int vbatt_pin = A1;
const int iled_pin = A2;
const int vled_pin = A6;
const int ipi_pin = A7;
int analog_pins[5] = {vbatt_pin,ibatt_pin,vled_pin,iled_pin,ipi_pin}; //collection of all analog pins


//digital pin assigments
const int pi_en_pin = 9; //control power to pi (but not 5V reg)
const int peri_en_pin = 8; //control 3.3V power to peripherals; ACTIVE LOW
const int hall_pin = 3; //for interrupts with hall sensor
const int signal_led_pin = 4; //on-board 0603 LED
const int alarm_pin = 2; //alarm from DS3231 RTC
const int pi_shdn_pin = 10; //pi shutdown control; HIGH = shutdown
const int fan_pin = 6; // for controlling fan


// for deployment mode
volatile int mode = 0;

// deploy time
// Note that RTC uses UTC TIME!!!
// UTC = PST + 7
int h_stt = 1; //deploy from 6pm to 6am 
int h_end = 13;
int m_stt = 17;
int m_end = 18;

// deploy status
int pi_status = 0; //indicate whether Pi is ON or not; default to OFF

void setup() {
  Serial.begin(9600);
  Serial.println("PUE Control Rev04");
  //digital pin setup 
  // all power control pins are INACTIVE by default
  pinMode(pi_en_pin,OUTPUT);
  digitalWrite(pi_en_pin,LOW);
  pinMode(signal_led_pin,OUTPUT);
  digitalWrite(signal_led_pin,HIGH);
  pinMode(pi_shdn_pin,OUTPUT);
  digitalWrite(pi_shdn_pin,LOW); 
  delay(1000);
  
  //peripheral control; the pin is active LOW
  pinMode(peri_en_pin,OUTPUT);
  digitalWrite(peri_en_pin,LOW);  //3.3V ON

  //initialize MS5837 sensor
  ms5837begin();
  // Initialize the BME280 sensor for temperture, pressure, humidity
  initBME280();

  mcp9808begin();
  // hall sensor interrupt
  attachInterrupt(digitalPinToInterrupt(hall_pin), pinISR, FALLING);

  //initialize TSYS01
  Wire.begin();
  temp_sensor.init();
  
  // RTC setup; print the time
  setSyncProvider(RTC.get);
  digitalWrite(signal_led_pin,LOW);
  Serial.println(now());
  printTime();
  
  delay(1000);
  //turn on RPi
  turnonPi();
  delay(2000);
}

void loop() {
  Serial.print(voltRead());
  sendData();
  delay(1000);
}
 




/***********************Helper Functions************************************/
void printTime(){
  Serial.print(hour());
  Serial.print(":");
  Serial.print(minute());
  Serial.print(":");
  Serial.println(second());
}

float battRead(){
  // read battery voltage
  float val = analogRead(vbatt_pin);
  return val/1024.0*3.3*2;
}

String voltRead(){
  /****** Read analog pins *******/
  //read values of all analog pins and construct a string to send via serial
  int n = sizeof(analog_pins)/sizeof(analog_pins[0]); //determine size of analog_pins first
  String dataString = String(now()); //initialize string here
  dataString += ",";
  for(int i=0;i<n;i++){
    //iterate over all analog pins
    int sensor = analogRead(analog_pins[i]); //read from each pin
    dataString += String(sensor); //add data to string
    dataString += ","; //delimited with a comma
  }

  return dataString;
}

void sendData(){
  // send BME280 data

  Serial.print(bme280Sensor.readTempC());
  Serial.print(",");
  Serial.print(bme280Sensor.readFloatHumidity());
  Serial.print(",");
  Serial.print(bme280Sensor.readFloatPressure());
  Serial.print(",");
  
  // send MS5837 data
  sensor.read(); //read data from MS5837
  Serial.print(sensor.temperature());
  Serial.print(",");
  Serial.print(sensor.pressure());
  Serial.print(",");

  // send TYSY01 data
  temp_sensor.read();
  Serial.print(temp_sensor.temperature());
  Serial.print(","); 
  
  // send MCP9808 data
  //tempsensor.wake();
  //Serial.print(tempsensor.readTempC()); //last one has to be println
  //Serial.print(",");
  Serial.println(millis());
  //Serial.println(0);
}

void shutdownPi(int thres){
  // send shutdown signal to RPi and then wait for current to drop and then cut pwr
  //Serial.println("shutdown"); //shutdown command
  digitalWrite(pi_shdn_pin,HIGH);

  digitalWrite(signal_led_pin,HIGH);
  
  delay(15000); //wait for Pi to shutdown
  //while(analogRead(ipi_pin)>thres) //wait for Pi to shutdown
  digitalWrite(pi_en_pin,LOW); //cut off power
  digitalWrite(signal_led_pin,LOW);
  pi_status = 0;
  digitalWrite(pi_shdn_pin,LOW);

}

void turnonPi(){
  //turn on RPi
  digitalWrite(pi_en_pin,HIGH);
  pi_status = 1;
}

void pinISR(){
  // hall ISR function
  digitalWrite(signal_led_pin,HIGH);
  delay(200);
  digitalWrite(signal_led_pin,LOW);
}

void blinkSignal(int n){
  for(int i=0;i<n;i++){
    digitalWrite(signal_led_pin,HIGH);
    delay(100);
    digitalWrite(signal_led_pin,LOW);
    delay(100);
  }
}

bool checkTimeHour(int hh_start, int hh_end){
  //check whether the time is between the specified hour
  int hh = hour(); // get current hour
  if(hh_end>=hh_start){
    //if the hour does not roll over a day
    return hh>=hh_start&&hh<=hh_end;
  }
  else{
    //if hour rolls over a day
    return hh>=hh_start||hh<=hh_end;
  }
}

bool checkTimeMin(int mm_start, int mm_end){
  //check whether the time is between the specified hour
  int mm = minute(); // get current hour
  if(mm_end>mm_start){
    //if the hour does not roll over a day
    return mm>=mm_start&&mm<=mm_end;
  }
  else{
    //if hour rolls over a day
    return mm>=mm_start||mm<=mm_end;
  }
}

/*******************I2C Sensors********************/

void mcp9808begin(){
  //initialize MCP9808 temperature sensor for LED temp monitoring
  tempsensor.begin(0x1F);
  tempsensor.setResolution(3);
}
void ms5837begin(){
  // Initialize MS5837 pressure sensor
  
  Wire.begin();

  // Initialize pressure sensor
  // Returns true if initialization was successful
  // We can't continue with the rest of the program unless we can initialize the sensor
  if (!sensor.init()) {
    Serial.println("MS5837 Init failed!");
  }
  else {
    Serial.println("MS5837 Init succeeded!");
  }
  
  sensor.setModel(MS5837::MS5837_30BA);
  sensor.setFluidDensity(1029); // kg/m^3 (997 freshwater, 1029 for seawater)
}


void initBME280()
{


    //commInterface can be I2C_MODE or SPI_MODE
    //specify chipSelectPin using arduino pin names
    //specify I2C address.  Can be 0x77(default) or 0x76
  
    //For I2C, enable the following and disable the SPI section
    bme280Sensor.settings.commInterface = I2C_MODE;
    bme280Sensor.settings.I2CAddress = 0x77;
  
    //For SPI enable the following and dissable the I2C section
    //bme280Sensor.settings.commInterface = SPI_MODE;
    //bme280Sensor.settings.chipSelectPin = 10;
  
    //runMode can be:
    //  0, Sleep mode
    //  1 or 2, Forced mode
    //  3, Normal mode
    bme280Sensor.settings.runMode = 3; //Forced mode
  
    //tStandby can be:
    //  0, 0.5ms
    //  1, 62.5ms
    //  2, 125ms
    //  3, 250ms
    //  4, 500ms
    //  5, 1000ms
    //  6, 10ms
    //  7, 20ms
    bme280Sensor.settings.tStandby = 0;
  
    //filter can be off or number of FIR coefficients to use:
    //  0, filter off
    //  1, coefficients = 2
    //  2, coefficients = 4
    //  3, coefficients = 8
    //  4, coefficients = 16
    bme280Sensor.settings.filter = 0;
  
    //tempOverSample can be:
    //  0, skipped
    //  1 through 5, oversampling *1, *2, *4, *8, *16 respectively
    bme280Sensor.settings.tempOverSample = 1;
  
    //pressOverSample can be:
    //  0, skipped
    //  1 through 5, oversampling *1, *2, *4, *8, *16 respectively
    bme280Sensor.settings.pressOverSample = 1;
  
    //humidOverSample can be:
    //  0, skipped
    //  1 through 5, oversampling *1, *2, *4, *8, *16 respectively
    bme280Sensor.settings.humidOverSample = 1;
    delay(10);  //Make sure sensor had enough time to turn on. BME280 requires 2ms to start up.         Serial.begin(57600);
  
    //Calling .begin() causes the settings to be loaded
    bme280Sensor.begin();

}

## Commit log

2020-03-30 Update for BES publication
    [IPAX BOM.xlsx, Optics Holder.stl, PCB Tray.stl, Simple Tube Holder v3.stl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]
2020-04-15 First upload building guide
    [ring_illuminator-Edge.Cuts.gbr, ring_illuminator-F.Cu.gbr, ring_illuminator-F.Mask.gbr, ring_illuminator-F.SilkS.gbr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]
2020-04-15 Update for revision05a
    [controlBoard_rev0401-B.Cu.gbr, controlBoard_rev0401-B.Mask.gbr, controlBoard_rev0401-B.SilkS.gbr, controlBoard_rev0401-Edge.Cuts.gbr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]

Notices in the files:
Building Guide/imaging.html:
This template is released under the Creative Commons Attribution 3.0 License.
